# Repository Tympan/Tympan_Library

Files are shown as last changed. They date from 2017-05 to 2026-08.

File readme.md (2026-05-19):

Tympan Library
===========================



**Purpose**: This library allows you to program your own audio processing algorithms for the Tympan!  It owes a big debt to the [Teensy Audio Library](http://www.pjrc.com/teensy/td_libs_Audio.html) and all of its contributors.

**Note**: These instructions were based on the *Arduino IDE 1.8.15* and *Teensyduino 1.54*. If you have different versions of either of these or have downloaded different versions, the program may or may not function as expected. You may revert or upgrade to the stated versions or check for solutions on the [Tympan Forum](https://forum.tympan.org/).

Requirements
------------

**Hardware**: All versions of the Tympan are, at their heart, compatible with the Teensy brand of microcontrollers.  Hence, many of the instructions below relate to Teensy.  For reference, Tympan RevD is Teensy 3.6 whereas the Tympan RevE is Teensy 4.1.

**Arduino IDE (Windows/Linux)**:  To program the Tympan, you need to download and install the 1.8.x version of the [Arduino IDE](https://www.arduino.cc/en/Main/Software).  Scroll down and download the 1.8.x version, do not use the newer 2.x version nor the web-based editor. After installing the Arduino IDE, open the shortcut so that it fully initializes.  Then, you can close it down and move to the next step, which is...

**Teensyduino Add-On (Windows/Linux, MAIN branch)**:  After installing the Arduino IDE, you need to download and install the [Teensyduino Add-On](https://www.pjrc.com/teensy/td_download.html), which allows you to program Teensy devices (including Tympan) using the Arduino IDE. It'll ask you whether you want to install a bunch of libraries.  You can say "yes" to them all, or you can say "yes" to these few: Audio, Bounce2, FreqCount, FreqMeasure, i2c_t3, SerialFlash, Snooze, and SPIFlash.  

**Teensyduino (Mac, MAIN branch)**: Recent versions of OS X do not support the Teensyduino Add-On installer, so there is a full [Teensyduino IDE](https://www.pjrc.com/teensy/td_download.html) available from the Teensy project which just needs to be downloaded and extracted from its ZIP file.

Installing the Tympan Library
------------

**Know GitHub?**:  If you know GitHub, go ahead and fork this repo and clone it to your local computer.  I strongly recommend that you clone it directly to the place on your computer where the Arduino IDE looks for libraries.  On my computer, I put them here: `C:\Users\chipaudette\Documents\Arduino\libraries\Tympan_Library`

**Don't Know GitHub?**: If you don't know GitHub, no problem!  You can download this library as a ZIP file.  Go back to the root of the Tympan library ([here](https://github.com/Tympan/Tympan_Library)) and click on the green button that says "Clone or Download".  You can then select "Download Zip".  Once the download is complete, I'd unzip the files and put them where the Arduino IDE looks for libraries.  On my computer, I put them here: `C:\Users\chipaudette\Documents\Arduino\libraries\Tympan_Library`

Connect the Tympan Audio Board
------------------

Open or restart the Arduino IDE. Before you can compile programs, you will need to tell the Arduino IDE that you want to program for Teensy. Under the "Tools" menu, choose "Board" and then "Teensy 4.1" for Tympan RevE (choose "Teensy 3.6" for Tympan RevD).  Also, under the "Tools" menu, choose "USB Type" and select "Serial + MIDI + Audio". 

If you haven't already, plug in the Tympan Audio Board to your computer using the micro USB cable. You will see orange lights. Power the unit ON using the white switch on the side and you will see the blue blinking light which indicates power. If you already had the Tympan Audio Board plugged in, turn the power off and then on again to power cycle prior to proceeding. Make sure you see the message that the device drivers are being installed.

Once your Tympan is connected to the computer via the micro USB cable and powered on, you can select the device by choosing "Port" under the "Tools" menu and and select the one that is associated with the Teensy (on Windows, it'll say "Teensy" in its name).

Try Some Examples
-------------

In the Arduino IDE, under the "File" menu, select "Examples".  Then, scroll way to the bottom of the list.  You should see an entry that says "Tympan_Library".  Those are all the example files for trying out different audio algorithms or features of the system.  I recommend starting with the basic examples:

* **Audio Pass-Thru:**  You should start with this example.  No processing, just an audio pass-thru from input (microphone, pink socket) to output (headset or earbuds, black socket).  You should always start as simple as possible.  It doesn't get simpler than this.  Since it doesn't apply any gain, it'll be quiet.

Once the example has been selected, it needs to be compiled or uploaded. The Arduino IDE's compile button is the one with the Arrow facing to the right. Note: take headphones off your ears when uploading a new program or changing modes to avoid any sharp pops, clicks, or other unpleasant noises.

Once the basic audio pass-thru program works, you can try the next example:

* **Basic Gain:** As your second trial, you try this example, which adds gain to the audio.  The blue volume knob adjust the amount of gain.  Easy!  

While the Tympan is connected to your computer (via USB) and running the Basic Gain example, you can communicate with your Tympan to find out what it's doing.  Under the Arduino IDE's "Tools" menu, select "Port" and select the one that is associated with the Teensy (on Windows, it'll say "Teensy" in its name).  Once you've selected the Teensy's port, you can open the "Serial Monitor" from the "Tools" menu.  On the Tympan, you can turn its blue volume knob.  Looking at the Serial Monitor window, you can see that it reports the volume setting it's now using.  In the other example programs, the Serial Monitor is used extensively to monitor what the Tympan is doing.

Once this works, you can work your way down the examples list to see how they add complexity and capability.  Have fun!

Releasing Tympan_Library to Arduino Library Manager
-------------
The Arduino "Library Manager" is a handy way for some users to keep up-to-date with the Tympan_Library.  For those of us used to using Git/GitHub, be aware that users do not get the latest state of the repository.  Instead, the Arduino Library Manager will only people's libraries if we do a new "Release" here on GitHub.  For Arduino to accept the release, however, you must do the release correctly:

* Make your desired changes to the Tympan_Library:
  * Commit your software changes to the repo and push them up here to GitHub
* Arduino-Specific Changes:
  * In the file [library.properties](https://github.com/Tympan/Tympan_Library/releases/new), update the version number to whatever new version number you intend to use.  Commit the change and push the change up here to GitHub.  If you forget to do this, Arduino will ignore the release.
* Do the GitHub release in the usual way:
  * Go to [Draft a New Release](https://github.com/Tympan/Tympan_Library/releases/new)
  * Under "Choose a Tag", start typing a name that you want to use for this Release ("V3.0.6").  Be sure to also click "Create New Tag on Publish" to tag the repo at its current state, which is what the release will be built on.
  * Fill in field for "Release Name" and add some text describing what is in the release
  * Click the button "Generate Release Notes", which puts a listing of all the commits at the bottom of the release text
  * Click "Publish Release"

To check on the status of the Tympan_Library being accepted by the Arduino Library Manager, see the Arduino processing log here: https://downloads.arduino.cc/libraries/logs/github.com/Tympan/Tympan_Library/

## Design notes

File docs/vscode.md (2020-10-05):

# Using VSCode and Platform IO with your Tympan

In addition to using the Arduino/Teensyduino IDE for working your Tympan, it is possible to use VSCode and PlatformIO as a development environment. It does, however, require some customizations to your `platformio.ini` file that might not be immediately obvious. The process for configuring VSCode and Platform IO (after you have followed the main instructions in the readme) is roughly as follows:

1. If you do not already have it, [download VSCode](https://code.visualstudio.com/download)
2. Install the [PlatformIO IDE plugin in VSCode](https://marketplace.visualstudio.com/items?itemName=platformio.platformio-ide) (note: if you use Anaconda on a Mac, you will likely need to update or reinstall Anaconda)
3. Create a new project in the PlatformIO IDE (choose the `teensy36` board)
4. Add the following three libraries to the lib_deps option: `Tympan_Library`, `https://github.com/PaulStoffregen/Audio.git`, and `https://github.com/PaulStoffregen/SD.git` (note: these are the same libraries required by the Tympan Library itself)
5. Put the path to the `libraries` directory you located in the "Installing the Tympan Library" section of the [readme](../readme.md) in the `lib_extra_dirs` option
6. Make sure to follow the instructions that PlatformIO gives you to convert your `.ino` file into a `.cpp` file (basically renaming the file and adding some additional `#include` directives)
7. Connect your Tympan to your computer and turn it on
8. Click the "Run" (right-facing arrow) button in the status bar to run your sketch on the Tympan

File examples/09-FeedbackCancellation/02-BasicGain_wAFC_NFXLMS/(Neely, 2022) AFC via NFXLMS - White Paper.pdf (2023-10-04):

Adaptive Feedback Cancelation
Introduction
Figure 1 shows a framework for adaptive feedback cancellation (AFC). The desired input signal is x(n), the actual microphone is d(n), and the hearing-aid output is s(n). When there is feedback, the microphone signal d(n) contains the feedback signal y(n) in addition to the desired signal x(n). The feedback signal is generated by the hearing-aid output s(n) passing through a feedback path F(z). The goal of feedback cancellation is to obtain an estimate of the feedback signal, denoted as y+(n), and subtract it from the microphone signal d(n) (Kates, 2008). This is achieved by placing a finite impulse response filter W(z) in parallel with the hearing-aid processing G(z). W(z) served as an estimate of the feedback path F(z). Under adaptive feedback cancellation, the coefficients of filter W(z) are continuously updated with the goal of emulating the impulse response of the feedback path F(z). Under ideal conditions, the estimated feedback path W(z) matches the actual feedback path F(z). When this happens, the feedback-compensated signal matches the feedback signal, so that y+(n) = y(n), and e(n) = x(n), i.e., the input to hearing-aid processing will not contain any feedback. In practice, however, AFC is not perfect, and some mismatch remains between e(n) and x(n), resulting in audible distortions.

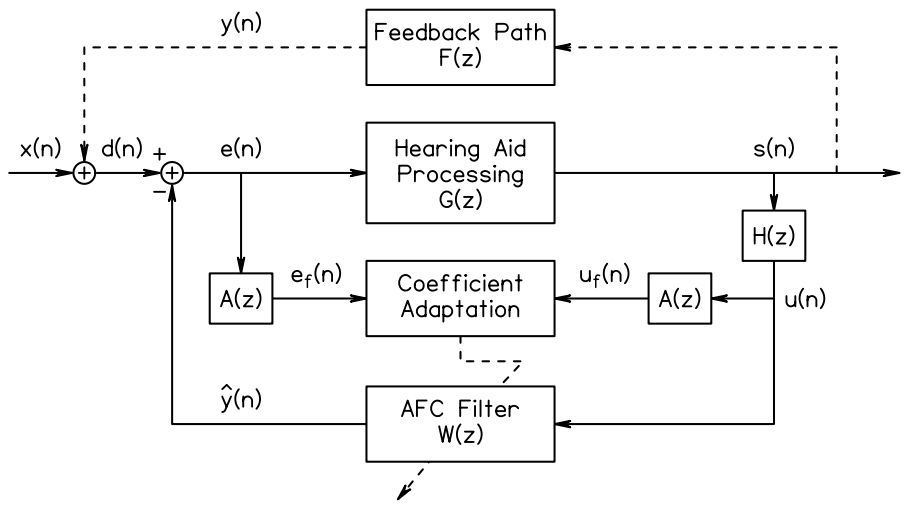
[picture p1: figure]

Fig. 1. Framework for adaptive feedback cancellation (Adapted from Lee et al. 2017). The actual and estimated feedback filters are F(z) and W(z), respectively. The whiten and band-limit filters are A(z) and H(z), respectively. The

The most common method for adaptive feedback cancellation is the least mean square (LMS) algorithm. Several LMS-based algorithms have been proposed, all of which include a step size parameter that controls how fast the AFC filter coefficients are updated. In the ordinary LMS algorithm, rapid fluctuations in the input signal can lead to instability. The normalized LMS (NLMS) algorithm mitigates some of the instability problems of the ordinary LMS algorithm by dividing the step size parameter by the signal power. For both NLMS and LMS coefficient adaptation method, the whiten and band-limit filters have unity gain, so A(z) = H(z) = 1. The normalized filtered-X LMS (NFXLMS) algorithms address some of the limitations of the NLMS method by (1) reducing non-feedback correlation and (2) concentrating adaptation on the frequency range where feedback is known to occur.

Normalized LMS
Normalized LMS (NLMS) is a variant of the LMS algorithm that improves stability by reducing sensitivity of coefficients to input signal level. The NLMS algorithm is based on cross-correlation between the output and input of the hearing-aid processing. The cross-product is weighted by a time-varying step size
w(n + 1) = w(n) + μ!(n)s(n)e(n).

The step is normalized by the signal power to improve convergence rate and stability
μ!(n) = "
℘(!)&' ,

where ℘(n) is a signal power estimate at time n and ε is a power-threshold parameter that prevents the denominator from becoming too small. In our implementation, the signal power is estimated by a first-order recursive equation
℘(n + 1) = ρ[s⁽(n) + e⁽(n)] + (1 − ρ)℘(n).

Note that the NLMS algorithm has three parameters: μ, ε, and ρ. Parameter values are optimized by minimizing the difference between the AFC filter W(z) and the feedback path F(z) in a simulated feedback configuration.
NFXLMS
When the NFXLMS algorithm is used to derive AFC coefficients the same calculations are performed as for NLMS except that u)(n) and e)(n) replace s(n) and e(n)

w(n + 1) = w(n) + μ!(n)u)(n)e)(n)

℘(n + 1) = ρ>u)

((n) + e)

((n)? + (1 − ρ)℘(n).

Additional filtering is required to obtain u)(n) and e)(n) from s(n) and e(n). Parameter values are optimized by minimizing the difference between the simulated feedback path F(z) and the product of W(z) and H(z). In practice, parameters are optimized by minimizing the mean-squared difference between the impulse responses f(n) and the convolution of w(n) and ℎ(n).

Whiten Filter
The whiten filter A(z) flattens the spectrum of the input signal x(n) to reduce correlation between the input signal and the hearing-aid output s(n). In our implementation, filter coefficients were derived from the long-term average speech spectrum (LTASS) described by Stelmachowicz (2000).
Figure 2 show the LTASS in the left panel and the inverted LTASS in the right panel (blue curve). The frequency responses of 5-tap and 9-tap linear-phase, FIR filters that approximate the inverse LTASS are superimposed (green and red curves). Each of these filters improve the AFC performance with relatively little increase in computational load.

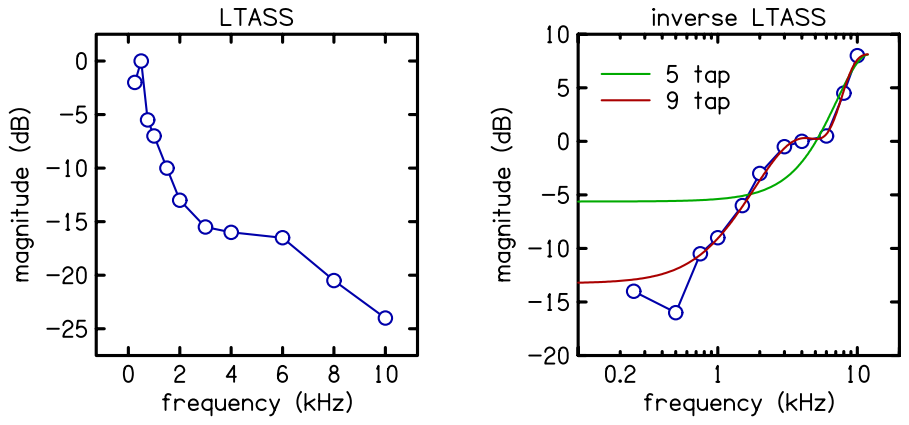
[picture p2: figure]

Fig. 2. Long-term average speech spectrum (LTASS) and its inverse. An inverse LTASS was constructed relative to the LTASS value at 4 kHz. The left panel superimposes 5-tap (green) and 9-tap (red) FIR approximations over the inverse LTASS (blue).
Band-limit filter
The motivation for the band-limit filter is to improve the efficiency of coefficient adaptation by focusing on the frequency range where feedback is known to occur. Our strategy is two-fold. First, we move some frequency dependence from W(z) to H(z). Second, we reduce the magnitude of H(z) at low frequencies where feedback is unlikely to occur.
The current implementation of the band-limit filter ℎ(n) has 36 taps and non-adaptive coefficients. The frequency response of the band-limit filter has a high-pass characteristic as shown by the green line in the right panel of Fig. 3. The effect of the band-limit filter on the AFC estimate of the feedback path is demonstrated in Fig 3 by observing that the estimated feedback (red) is closer to the actual feedback (black) in the right panel compared to the left panel.

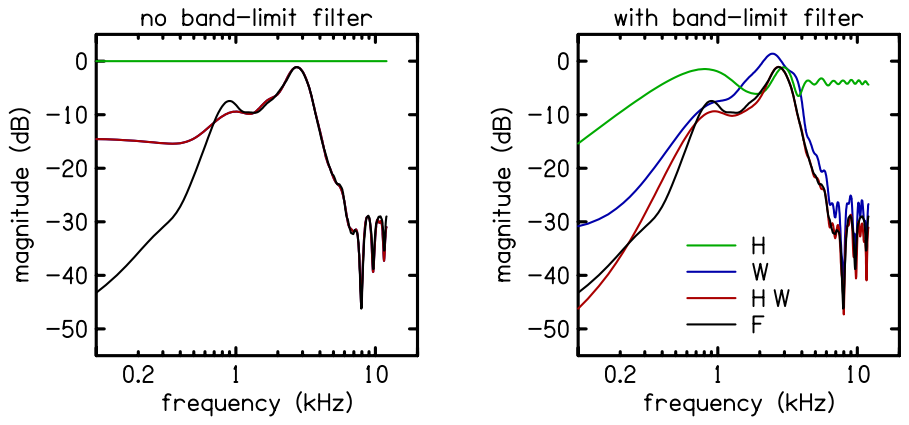
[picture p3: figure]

Fig. 3. Spectral magnitudes of the band-limit (H, green), AFC (W, blue), and feedback-path (F, black) filters. Also shown is combined response of the product of the band-limit and AFC filters (HW, red), which approximates the feedback-path filter. For the case without band-limiting (left panel), the band-limit filter has 0 dB gain at all frequencies. When band-limiting is applied (as described in the text), the combined response (red) better estimates the feedback-path (black) below 0.4 kHz and above 8 kHz.

Parameter Values
Optimization of parameter values was based comparison of the actual feedback path with the AFC estimate. An estimation error was defined as the mean-squared difference between the actual and estimated feedback-path impulse response. The estimation error was computed as a function of time for the “carrots” passage, which is 13 seconds long. Parameter values were selected (by a simplex search) to minimize the maximum error over the interval of time between 2 and 13 seconds. Figure 4 illustrates the parameter optimization procedure by comparing an example of actual and estimated feedback paths (left panel) and by showing an example of time course of the estimation error (right panel).

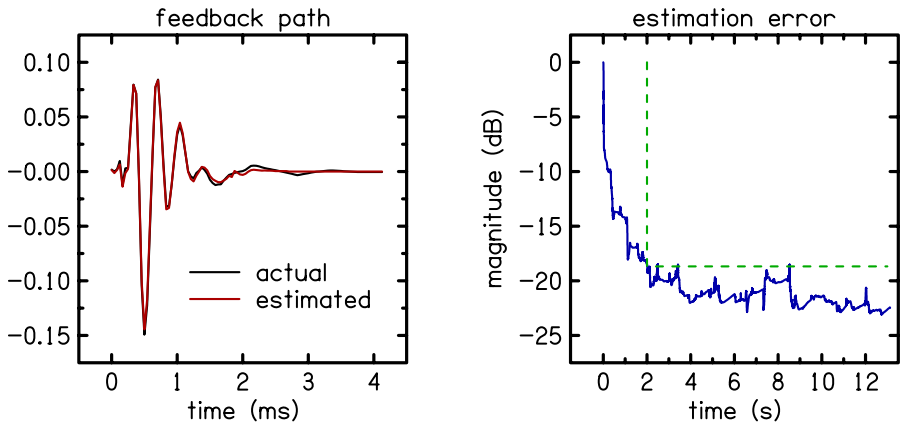
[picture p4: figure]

Fig. 4. Comparison of the actual (black) and estimated (red) feedback-path impulse responses (left panel) and the time course of the estimation error (right panel). The dashed (green) line (right panel) indicates the maximum-observed error over the interval of time between 2 and 13 seconds.
The four parameters optimized by this procedure appear in the equations used to calculate the AFC filter coefficients (μ, ε, ρ) and the band-limit filter coefficients (α). Filter lengths were also varied independently in a stepwise manner to further the estimation error. The following Table summarizes the results of parameter optimization.
AFC Filter | Whiten Filter | Band-limit Filter | ρ | ε | μ | Error (dB) | Comp time
42 | 0 | 0 | 0.000002 | 0.001395 | 0.000418 | -13.58 | 0.164
42 | 9 | 0 | 0.006840 | 0.001178 | 0.004693 | -15.27 | 0.165
42 | 9 | 20 | 0.007219 | 0.000919 | 0.004607 | -18.47 | 0.441

The first set of parameter values in the Table represent our NLMS algorithm which has no whiten or band-limit filters. The second set of parameters shows a reduction of 1.7 dB in the estimation error when a whiten filter is added to NLMS. The third set of parameters represents the addition of both whiten and band-limit filters, which represents our NFXLMS algorithm and shows a 5.2 dB reduction in estimation error relative to our NLMS algorithm. We hope to see a corresponding 5.2 dB improvement in added stable gain (ASG).

References
Kates, J. M. (2008). Digital hearing aids. Plural publishing, pp 175-220.
Lee, C. H., Kates, J. M., Rao, B. D., & Garudadri, H. (2017). “Speech quality and stable gain trade-offs in adaptive feedback cancellation for hearing aids,” J. Acoust. Soc. Am. 142, EL388-EL394.
Stelmachowicz, P. G. (2000). “How do we know we’ve got it right? Electroacoustic and audiometric measures,” in “A sound foundation through early amplification,” proceedings of an international conference, pp. 109-118.

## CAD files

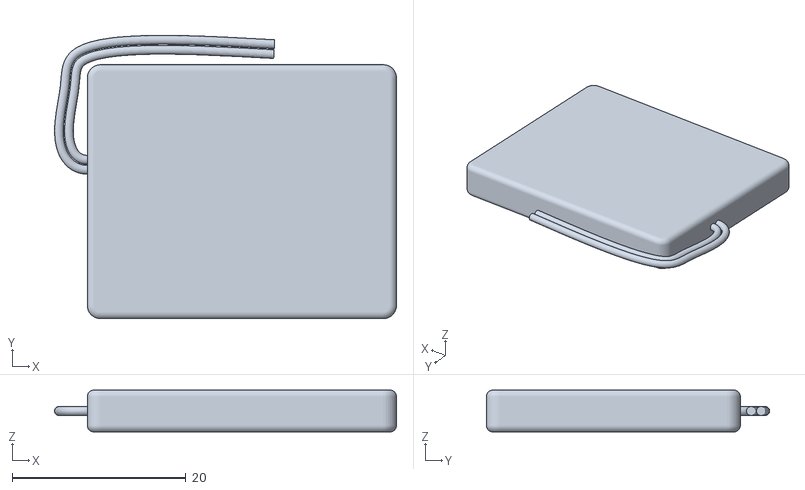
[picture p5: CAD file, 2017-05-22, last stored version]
hardware/Tympan_Enclosure/SolidModelOfPCB/Lion Ion Battery.stl
39.3 x 32.6 x 4.83

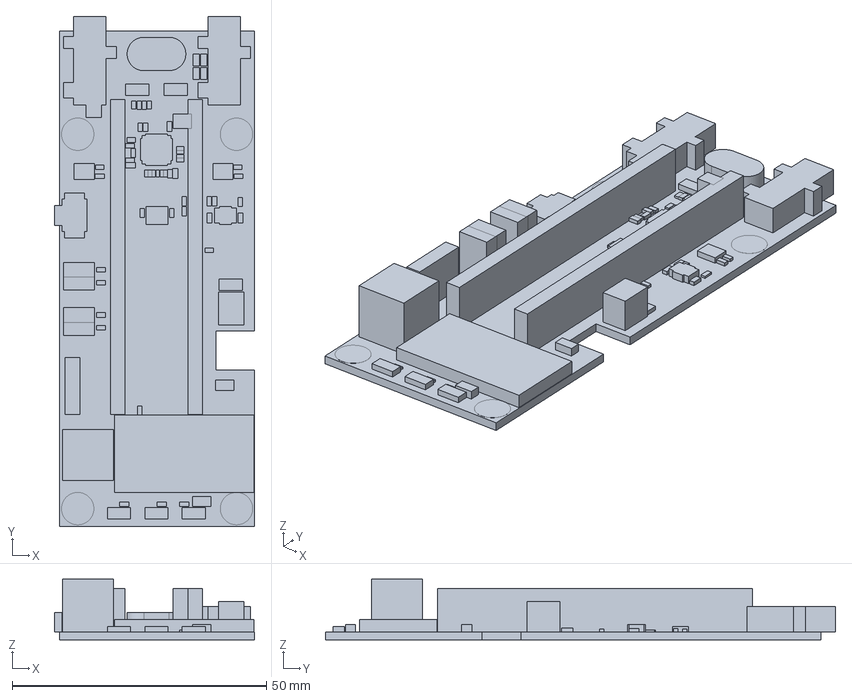
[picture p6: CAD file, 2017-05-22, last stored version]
hardware/Tympan_Enclosure/SolidModelOfPCB/7146-0012_PCB_Rev-A.STP
39.4 x 100.3 x 12.0 mm
BOARD_OUTLINE
COPAL_CL-SB-22A-1
RESC1609X50N x 4
SAMTEC_SSW-124-XX-X-S x 2
SAMTEC_SSW-104-XX-X-S
SAMTEC_SSW-101-XX-X-S
SLOT1000X500MECH
FUSC3216X78N
MTG_4 x 4
MICROCHIP_RN42
TP340X180N x 2
PH_B2B-PH-K-S
RESC0603X26N x 10
RESC100X50X40L25 x 2
RESC1005X40N x 8
SAMTEC_SSW-102-XX-X-S x 4
CAPC1005X55N x 13
LEDC3216X110N x 5
CAPC1005X70N x 5
CAPC1005X65N x 8
BOURNS_3386F-KNOB
CUI_SJ-3523-SMT
CUI_SJ-3524-SMT
SOT23-5P95_270X145L35X35
SOT95P280X145-5N
KNOWLES_SPH1642HT5H-1 x 2
QFN40P500X500X80-41N

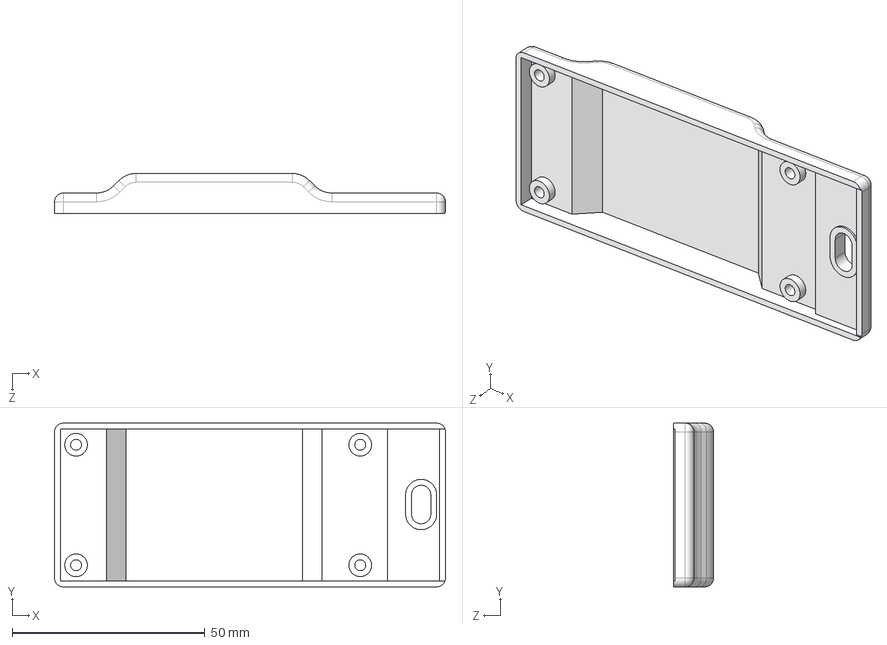
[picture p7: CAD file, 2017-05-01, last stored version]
hardware/Tympan_Enclosure/STEP/10000167 rev3.step
101.3 x 42.4 x 10.4 mm

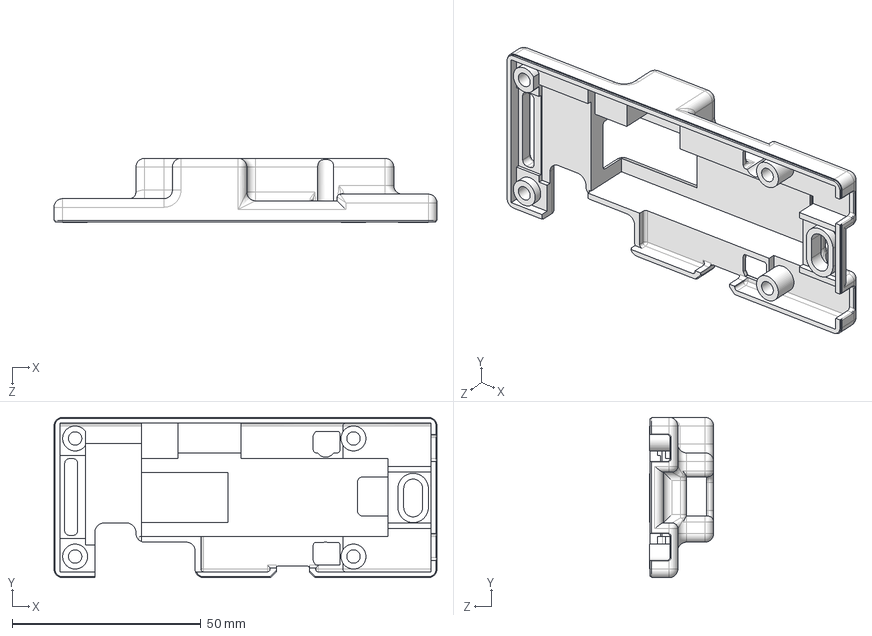
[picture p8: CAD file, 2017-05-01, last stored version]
hardware/Tympan_Enclosure/STEP/10000200_r2.step
101.3 x 42.4 x 17.0 mm

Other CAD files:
hardware/Tympan_Enclosure/SolidModelOfPCB/Lithium Ion Battery.step
hardware/Tympan_Enclosure/STL/10000167 rev3.stl
hardware/Tympan_Enclosure/STL/10000200_r2.stl

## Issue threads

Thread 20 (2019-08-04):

Tympan/Tympan_Library #20: failed build with 05-FullSystems/* example sketches, one error and others too large

shapr, 2019-08-04:
I'm using Ubuntu 19.04 with Arduino 1.8.9 and Teensyduino 1.46
and the very latest git clone of Tympan_Library

I've failed to compile all of the 05-FullSystems/*

* WDRC_8BandFreqWarpFIR:45: error: 'audioTestMeasurement' was not declared in this scope AudioControlTestAmpSweep_F32    ampSweepTester(audio_settings,audioTestGenerator,audioTestMeasurement);
* File "WDRC_8BandIIR_wBT.ino.hex". 74520 bytes, 116% used
* File "WDRC_8BandIIR_wBT_wAFC.ino.hex". 89688 bytes, 139% used
* File "WDRC_8BandFIR_wBT.ino.hex". 85568 bytes, 133% used
* File "WDRC_8BandFIR.ino.hex". 85056 bytes, 132% used
* File "WDRC_3BandIIR_wBT_wAFC.ino.hex". 88672 bytes, 137% used

I haven't dug into the actual compile error, but the others all claim they resulting sketch is too large to fit onto the chip.
Perhaps this is something to do with the Teensyduino 1.46 update?

chipaudette, 2019-08-05:
I'm sorry for the basic question back to you...but In the Arduino software, under the "Tools" menu, did you change your "Board" to "Teensy 3.6"?  

Chip

chipaudette, 2019-08-05:
Also, I fixed the error with the WDRC_8BandFreqWarpFIR as of commit f9d82558f8304a24e2d246bbf261f2f0a3855493

Good find!

As for the memory issue, please see my comment above.  If you're not set for Teensy 3.6, it is very easy to see how it thinks you won't have enough memory.

Chip

shapr, 2019-08-06:
I fired up the Arduino IDE and checked my settings (I'm using WDRC_8BandIIR_wBT since I believe that's the default firmware).
I do have the "Teensy 3.6" board selected (basic questions are fine, I make mistakes all the time!)
In the process, I discovered the Arduino menu has "Tools" -> "Optimize" and the "faster" option was selected. Once I selected "smallest", the Teensyduino loader stops complaining.

Should the code fit on the board with the "faster" option selected? 
I also tried "fast" and "fastest" but once the hex file reaches the teensyduino loader I get "too large".

chipaudette, 2019-08-08:
I finally found someone here who uses Ubuntu.  We're going to try to recreate your problem...

jdw-creare, 2019-08-08:
@shapr , I was able to reproduce your issue.  I've reported it to the Teensy maintainers here: https://github.com/PaulStoffregen/Arduino-1.8.9-Teensyduino/issues/3

closed 2019-09-28 by wheresaddie

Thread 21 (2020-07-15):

Tympan/Tympan_Library #21: External Delay

finnwoodman, 2020-07-15:
Hej Tympan Crew, 
I just stumbled across your incredible audio board. It looks like the perfect alternative for what I am doing with the teensy audio board right now. I was wondering whether Tympan has the capabilities to use something to Teensy Audio's AudioEffectDelayExternal. This allows creating longer lasting delays by using additional memory – either placed on the pcb directly or by incorporating a custom memory board. 
Best regards, Max

biomurph, 2020-07-15:
@finnwoodman @chipaudette 
So glad you found us!
I'm pinging Chip, who will be able to help answer.
Tympan works with the teensy audio library, and we have an SD card slot on board, if that is fast enough for your needs. If SD is too slow, we have breakout pins for the SPI bus, so you can lash up a flash memory chip or other.

What is your project and speed/memory needs?

finnwoodman, 2020-07-15:
Thank you for your fast reply. I guess SD card will be to slow as I am processing live sound. So, what I want to create is a 2sec echo loop of a microphone input. The overall goal is creating a kind of simple loop machine.

I managed to create such a "Machine" using the teensy audio board and external ram. Nevertheless I am facing a lot of noise. Tympan looks promising regarding noise and co...

biomurph, 2020-07-15:
Great video!
And great machine.

Adafruit has a couple flash breakouts. Here's one
https://www.adafruit.com/product/1895
It's I2C, and we've broken out the I2C on the Tympan. Note the lower left corner of the Tympan D [schematic](https://github.com/Tympan/Tympan_Rev_D_Hardware/blob/master/TympanRevDschem.pdf) which corresponds to the pinout looking down on the Tympan board. There are lots of development modules that use SPI as well if you really need speed.

I've had parts on my bench for a while to build an effects pedal with a Tympan D. Sparkfun has a nice [kit](https://www.sparkfun.com/products/13124) and I plan to use a flash memory chip in it. Just need the time to work out the power supply...

chipaudette, 2020-09-09:
@finnwoodman, currently the hardware has no place to add external memory.  So, you have the same memory as a Teensy 3.6.

If you need additional RAM, you'll need a product like the blackaddr Teensy Guitar Audio Shield: http://blackaddr.com/products/.  It has options that you can include when you place your order to add a 4Mbit or 8Mbit memory IC.

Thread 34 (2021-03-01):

Tympan/Tympan_Library #34: USB audio not supported

hriday91, 2021-03-01:
Currently USB audio in/out is not supported by tympan. Any idea on when will it be supported?

chipaudette, 2021-03-01:
Hi!  

USB audio could be supported as long as you always use a 44kHz sample rate with 128 points per audio block.  Its this inflexibility in the underlying Teensy USB audio system that is the problem.

Would 44 kHz / 128 points meet your needs?

Chip

chipaudette, 2021-06-10:
I would like to wrap the Teensy's USB audio class in a Tympan "_F32" wrapper.  I did this before, but it would cause compiler warnings if you didn't set your Arduino IDEA to have the "USB Type" include audio.  Since most people didn't use the USB audio, this was an annoying warning, so I pulled the _F32 wrapped USB audio class out of the Tympan Library

I think that there is a way for our code to listen compiler flags to avoid these warning messages so that we know if USB Audio has been set in the Arduino IDE.  If I can find out how to do that, we can put the _F32 USB audio class back in our library.

It's on the To-do list, for sure.

nithinr07, 2021-06-21:
Hi,

I am trying to add an AudioOutputUSB block to the single-channel WDRC code. However, this code can't really run well on the Rev D with the 44.1kHz and 128 block size setting, so I was wondering if there is any way to send the audio through USB at lower sampling rates.

Thanks!

chipaudette, 2021-06-21:
The USB audio functionality is the exactly the same code as the Teensy Audio Library USB audio code.  That code is limited to 44.1kHz and 128-sampke block size.  Sorry.

Does the FreqDomainDemo example that I linked above work ok?  Is your problem occur only when you use the USB audio with the WDRC?

nithinr07, 2021-06-21:
Yes, as long as the sampling rate is 44.1KHz and the audio block size is 128, it works, but unfortunately, the 8 band WDRC code can't support this on the Rev D I believe.

chipaudette, 2021-06-21:
You are correct.  the 8-band WDRC consumes too much CPU to be performed at 44 kHz.  If you want the USB audio, you will have to use fewer bands.

There is a group in Montreal that is looking to dig deep into the Teensy Tympan USB Audio code (and, therefore, the Tympan USB Audio code) to make it more flexible so that it can support different sample rates.  If they do it, I believe they are planning on doing it in July - September.

nithinr07, 2021-06-21:
Also, just to point out, I noticed that there were distinct "clicks" in the USB output when the sampling rate was 44100 Hz. However, this problem was solved when I changed the sampling rate to 44117 Hz.

chipaudette, 2021-06-21:
Yes, the requirement for 44117 is part of the limitations (and odd behaviors) that come with the Teensy audio library.  

Sorry.

nithinr07, 2021-06-28:
Hello again!

So, I managed to make the Tympan run at 24,000 Hz / 128 sample block size by tweaking the Teensy library (the USB descriptors), but I wasn't able to lower the block size. I noticed that the WDRC code performs best at lower block sizes, so I was wondering if you could provide me with any leads regarding this. 

Nithin

chipaudette, 2021-06-28:
Wow!  Congratulations on gettng the lower sample rate to work over USB!  Very impressive!

As for shorter block sizes, the WDRC is actually more computationally efficient (ie, less CPU consumed) for the larger block sizes like 128.  What works better is that the latency (the delay) of the audio passing through the system is reduced if the block size is made smaller.  

Do you care about latency?

  * If you do NOT care, than your 128-point block size should be great!
  * If you do care, then you should look into changing the Teensy header file [AudioStream.h](https://github.com/PaulStoffregen/cores/blob/adca415331771bbf1560d7a008ccb150b0ec603a/teensy3/AudioStream.h).  Change AUDIO_BLOCK_SIZE from 128 to something smaller (and change the Tympan code to match) and it might work for you.

Let me know how it goes!

Chip

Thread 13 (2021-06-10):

### ISSUE TITLE
No delay needed after Wire.write().

### ISSUE THREAD

**Issue by Koepel** [Tympan/Tympan_Library#13]
In the file "Tympan_Library/src/control_tlv320aic3206.cpp", there is sometimes a delay() after a Wire.write(). I think that delay() can be removed.

It is similar to this:
```
int i = 3;
delay(10);  // wait until i becomes 3
int j = 5;
delay(10);  // wait until j becomes 5
```

In the Arduino Wire library and in most Arduino Wire compatible libraries, a buffer is used. The Wire.beginTransmission() resets the buffer, the Wire.write() fills the buffer and the Wire.endTransmission() does the complete I2C transaction with START, I2C address, write data from the buffer and STOP.

I took a quick glance at the TLV320AIC3206 datasheet, but I can't read that a delay would be needed somewhere.

**Comment by chipaudette** [comment]
Over the last several years, I think that we have now pulled out most of the delay() calls.  There are a few delay() calls left in there, but they are mostly after register settings that change how the hardware functions, so they are there to let the hardware settle.

I think that this is complete.

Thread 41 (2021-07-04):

Tympan/Tympan_Library #41: Wrong register values for Mic Bias

eyuan-creare, 2021-07-04:
Value for 1.7V mic bias is not offset to the correct bits

Here is the register for Mic Bias (AIC3206), showing bias voltage as bits D5-D4. For example, to set Mic Bias to 1.7V, we need `TYMPAN_MIC_BIAS_POWER_ON   |  0b0001 0000`

[image]

- However in [Tympan Library](https://github.com/Tympan/Tympan_Library/blob/c44b8c3d6fce48084498e54583e6e4b5d78af186/src/control_aic3206.cpp#L162) the values are not shifted to the correct bits, either in the #define or the wrapper function 
```
#define TYMPAN_MIC_BIAS_REG 0x0133 // page 1 reg 51
#define TYMPAN_MIC_BIAS_POWER_ON  0x40
#define TYMPAN_MIC_BIAS_POWER_OFF 0x00
#define TYMPAN_MIC_BIAS_OUTPUT_VOLTAGE_1_25     0x00
#define TYMPAN_MIC_BIAS_OUTPUT_VOLTAGE_1_7      0x01
#define TYMPAN_MIC_BIAS_OUTPUT_VOLTAGE_2_5      0x10
#define TYMPAN_MIC_BIAS_OUTPUT_VOLTAGE_VSUPPLY  0x11
```

- Here is the [setMicBias](https://github.com/Tympan/Tympan_Library/blob/c44b8c3d6fce48084498e54583e6e4b5d78af186/src/control_aic3206.cpp#L287) function.  When 1.7V is selected this results in a value of `0b0100 0001` instead of 0b0101 0000
` aic_writeAddress(TYMPAN_MIC_BIAS_REG, TYMPAN_MIC_BIAS_POWER_ON | TYMPAN_MIC_BIAS_OUTPUT_VOLTAGE_1_7); // power up mic bias
`
So I believe the way it is now, if you select 1.25V that's fine.  But if you select 1.7, 2.5V, or the power supply, then you actually get 1.7V, with bit-0 set (which is reserved) 

@chipaudette perhaps you can double-check this, then I will branch off to make these corrections.  Does this mesh with the behavior you've seen?

eyuan-creare, 2021-07-04:
I don't think it is worth changing for the AIC3212, but I would typically use enums [here](https://github.com/Tympan/Tympan_Library/blob/c44b8c3d6fce48084498e54583e6e4b5d78af186/src/control_aic3206.h#L32).  This allows coders to quickly look up the enum from the function's input argument, and ensures that only the correct range of values are used.  With #defines, it is difficult to search for which define to use, unless you go off an example.
```
//names to use with setMicBias() to set the amount of bias voltage to use
#define TYMPAN_MIC_BIAS_OFF             0
#define TYMPAN_MIC_BIAS_1_25            1
#define TYMPAN_MIC_BIAS_1_7             2
#define TYMPAN_MIC_BIAS_2_5             3
#define TYMPAN_MIC_BIAS_VSUPPLY         4
#define TYMPAN_DEFAULT_MIC_BIAS TYMPAN_MIC_BIAS_2_5
```

to 

```
typedef enum {
    off, 
    Mic_Bias_1_25V, 
    Mic_Bias_1_70V,
   ...
} Mic_Bias_Values_t;
```

then in the function...

```
bool AudioControlAIC3212::setMicBias(Mic_Bias_Values_t biasSetting) {
  switch (biasSetting){
        case Mic_Bias_1_25V:
           aic_writeAddress(TYMPAN_MIC_BIAS_REG, TYMPAN_MIC_BIAS_POWER_ON | TYMPAN_MIC_BIAS_OUTPUT_VOLTAGE_1_25); // power up mic bias
          break;
    }
}
```
<br><br><br>
To take it a step further, I would encode the register value for mic bias voltage like this:
```
typedef enum {
    uint8_t Mic_Bias_1_25V = 0x00, 
    uint8_t Mic_Bias_1_70V = (0x01<<4) ,
    ...
} Mic_Bias_Voltage_t;
```

then in the function:
```
bool AudioControlAIC3212::setMicBias(Mic_Bias_Voltage_t biasSetting) {
    uint8_t regValue = 0;

    // Read in what's there to preserve the other bits 
   regValue  =  aic_ReadAddress(TYMPAN_MIC_BIAS_REG);

   // Mask out the desired bits to change
   regValue &= (~MIC_BIAS_VOLTAGE_BIT_MASK); 
  
    // Write the new register value
    aic_writeAddress(TYMPAN_MIC_BIAS_REG, regValue | biasSetting);
}
```
I think this is much cleaner.

eyuan-creare, 2021-07-04:
In regards to the AIC3212, it uses different mic bias voltage.  Is that an issue with any of our mics?

[image]

chipaudette, 2021-07-04:
We've only ever used the full bias voltage (2.2v?), so these other voltage values have never ended up being an issue.  It's good to get them correct, but it's not yet been revealed as a problem die to always using the full voltage.  

I agree that an enum send better.  Someone else did the initial code where #define was used instead of enum.  Enum seems better.

Chip

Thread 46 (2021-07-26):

Tympan/Tympan_Library #46: BluetoothAudio_PassThru - Cannot Connect RevE

hgeithner-creare, 2021-07-26:
The Tympan RevE does not show up as an audio device on the phone (Android/iOS) when the BluetoothAudio_PassThru sketch is loaded on the Tympan.

Testing instructions:

- Open your phone's Bluetooth control panel and connect to the Tympan manually
- Open any audio-related app on your phone (or a browser and then to YouTube)
- Play something with audio
- Plug headphones in the Tympan and you should hear your phone's audio through the Tympan
- The volume buttons on your Phone should affect the phone's audio coming out of the Tympan

At the same time, you should be able to tap on the case of the Tympan and hear the Tympan's own microphones mixed with the BT audio.

chipaudette, 2021-07-26:
With the v5 firmware for the BC127, I got bluetooth audio to work simply by invoking the sparkfun library, which is discussed in their helpful tutorial here:

https://learn.sparkfun.com/tutorials/understanding-the-bc127-bluetooth-module/all#usage-examples

It says that they used the Advanced Audio Distribution Profile (A2DP) and Audio/Visual Remote Control Profile (AVRCP) profiles to do the remote audio connection.  It's likely that only A2DP is needed to make the audio flow if one is always driving the play/stop/volume from the phone itself (rather than having the Tympan itself command "play" or "stop" of the audio, which is done via AVRCP).

In the v7 firmware, maybe some other protocol is better, but I'd start by looking at how to enable A2DP.

chipaudette, 2021-07-26:
Melody (ie, BC127 Firmware) V7 Documentation for A2DP:
 
[image]

chipaudette, 2021-07-26:
It looks like that "SET PROFILES=0 0 1 0 1 0 0 0 0 0 0 0" is the key line that we need to convey during initialization of the BC127.  What does each zero or one correspond to?  According to the table below, it permits one A2DP sink connection and one AVRCP connection.

[image]

chipaudette, 2021-07-26:
Based on the table above, it looks like "A2DP sink" should already be enabled (has a "2").  Why doesn't it?

chipaudette, 2021-07-26:
Apparently A2DP is an BT Classic feature whereas we have been (recently) only focusing on BLE.  We enable BLE connections by commanding "ADVERTISING ON" but this does nothing to enable the classic BT connections.  Therefore, we must also enable the BT classic modes to be connectable and discoverable via the command:

`BT_STATE ON ON

This is necessary for the V7 firmware.  I'm not sure about the V5 firmware.

hgeithner-creare, 2021-07-26:
I'm not sure that it would be necessary for the V5 firmware because I was able to connect the RevD.

chipaudette, 2021-07-26:
Ray already included a command for "discoverable()" in the BC127 library.  This command only works for V5.  I extended it for V7.  I also altered the BLE class to initialize the module to make it discoverable (BT classic) by default upon startup (and anytime, actually). 

Changes are on feature_BTaudio branch.

This enables a simultaneous BT audio and BLE connection.  The problem is that it still won't receive audio (on my BC127 HD running V7.3HD).  Whenever I start to stream audio to it, the module appears to reset.  :(

chipaudette, 2021-07-26:
It appears that the unit defaults to allow for the GPIO pins to control the system operation, such as when sinking audio.  Since I am not consciously controlling the BC127 pins, maybe it is getting confusing commands?  Let's try disabling the GPIO control via (v7 firmware):

`SET GPIO_CONFIG=OFF 0`

Then write then reset.

Now, the BC127 seems to lock up instead of just resetting.  I have to cycle the power to get the BC127 to respond again.

chipaudette, 2021-07-26:
When you set GPIO_CONFIG to "off", it doesn't disable GPIO control, it merely alters it...one pin is still an input:

[image]

chipaudette, 2021-07-26:
On RevE, PIO 4 is not connected to anything...meaning it is floating...meaning it is high impedance...meaning the BC127 should be fine with driving it as an output.

PIO 0 and PIO 5 are connected to pins on the Teensy.  When I manually configure them so that the Teensy treats PIO 0 as an input (ie, makes it high impedance) and treats PIO 5 as an output set low (ie, forces it to exit data mode), the system no longer freezes when I start streaming audio.   Instead, it merely returns to the same behavior as before...it fails to stream (ie, no audio comes out the headphone jack) and it stops my phone music app after ~3 seconds.

Still in search of a solution...

chipaudette, 2021-07-26:
I'm stumped.  Here's my test method:

I'm using the example sketc below, based on BC127Terminal, but with added '\r' -> '\n' reformatting to allow use of the Arduino Serial Monitor:

```
/*
*	BC127Terminal
*
*	Created: Ira Ray Jenkins, Creare, December 2020
*	Purpose: Demonstrates a serial terminal with the BC127 module.
*
*/

#include <Arduino.h>

usb_serial_class *USB_Serial;
HardwareSerial *BT_Serial;

void echoIncomingUSBSerial(void)
{
    while (USB_Serial->available())
    {
        BT_Serial->write(USB_Serial->read());
    }
}

void echoIncomingBTSerial(void)
{
  char c;
    while (BT_Serial->available())
    {
      c = BT_Serial->read();
      if (c == '\r') c = '\n'; //replace carriage return with newline to make pretty in Arduino Serial Monitor
      USB_Serial->write(c);
    }
}

void setup()
{
    //  myTympan.beginBothSerial();
    Serial.begin(9600);
    Serial1.begin(9600);
    USB_Serial = &Serial;
    BT_Serial = &Serial1;

    Serial.println("Setting GPIO pins that are connected to BC127 assuming SET GPIO_CONTROL=OFF 0");
    pinMode(2,INPUT);  digitalWrite(2, LOW); //RevE PIO5
    pinMode(5,OUTPUT);//RevE PIO0

    Serial.println("Type commands to send to the BC127.  Be sure to use carriage return, not newline...");
}

void loop()
{
    echoIncomingUSBSerial();
    echoIncomingBTSerial();
}
```
Test Steps with RevE (with V7.3HD firmware):

0) The first time you do this, have your phone "forget" your Tympan BT unit
1) Compile and upload the sketch.
2) Open the Serial Monitor
3) Type Status.  Do you see `STATE CONNECTED[0] CONNECTABLE[ON] DISCOVERABLE[ON] BLE[IDLE]`.  If not:
    * type: SET BT_STATE_CONFIG=1 1
    * optionally, type: SET GPIO_CONFIG=OFF 0
    * type: WRITE
    * Type: RESET
4) Pair your phone and Tympan (the first time)
5) In your phone's BT control panel, connect to the Tympan
6) In the serial monitor, you should have seen stuff happen.  Type STATUS to see the connections
7) Open a music player app on your phone and stream music

Assuming that it fails for you, like it did for me...It should run for a ~3 seconds before the app switches to pause.  In the serial monitor, you should see the startup text, like:

```
Sierra Wireless Copyright 2018
Melody Audio V7.3 HD
Build: 1544717993
Ready
CHARGER_DISABLED
```

Bummer.

ijenkins-creare, 2021-08-04:
@hgeithner-creare , Haley, could you create a new sketch from Chip's example above. Compile for the RevE:v7. Once running, bring up the serial monitor, change the newline to carriage return (the dropdown menu left of "Clear output"). All of the following commands are entered via the serial monitor input line.

Enter "STATUS". You should see something like: 
```
STATE CONNECTED[0] CONNECTABLE[OFF] DISCOVERABLE[OFF] BLE[IDLE]
```

If not, what do you see? Try a "RESTORE" command.

Next, toggle BLE mode on with the command "ADVERTISING ON". Should see "OK". Check that the "STATUS" changed.

At this point, you should be able to connect to the Tympan from a phone/tablet via BLE. Assuming that connection is fine, you should see something like:
```
OPEN_OK 14 BLE 63F5A35DDBB5
```
Next, you can enter the command "BT_STATE ON ON", and again check your phone/tablet for bluetooth connections. You should see the same device name, but with *maybe* a different icon? Try to connect to it. Hopefully it spits out something like:
```
OPEN_OK 23 HFP 90B1445F6B2C
ROLE_OK 90B1445F6B2C M
OPEN_OK 20 A2DP 90B1445F6B2C
ROLE_OK 90B1445F6B2C M
A2DP_STREAM_START 20
OPEN_OK 21 AVRCP 90B1445F6B2C
ABS_VOL 21 77
A2DP_STREAM_SUSPEND 20
AVRCP_PAUSE 21
A2DP_STREAM_START 20
AVRCP_PLAY 21
```
Play some music or video files. You won't be able to hear audio, but you should see in the serial monitor that "something" happens. Let it play for a minute, making sure the phone doesn't pause the video/audio and the serial monitor doesn't "stall". You can periodically type "STAUS" just to make sure it's still alive, if you like.

Thanks!

hgeithner-creare, 2021-08-05:
@ijenkins-creare I load the example sketch and the STATUS looks good:

```
08:49:19.989 -> Setting GPIO pins that are connected to BC127 assuming SET GPIO_CONTROL=OFF 0
08:49:19.989 -> Type commands to send to the BC127.  Be sure to use carriage return, not newline...
08:49:19.989 -> STATE CONNECTED[0] CONNECTABLE[OFF] DISCOVERABLE[OFF] BLE[IDLE]
08:49:20.082 -> OK
```
BLE ADVERTISING successful: 

```
08:49:40.582 -> OK
08:49:54.607 -> STATE CONNECTED[0] CONNECTABLE[OFF] DISCOVERABLE[OFF] BLE[ADVERTISING]
```

When I pair the device:

```
08:50:51.202 -> OPEN_OK 14 BLE 5A2AF556C6FE
08:50:51.342 -> PAIR_PENDING
08:50:56.606 -> PAIR_OK D4E6B726F4F8
08:50:56.653 -> BLE_PAIR_OK 5A2AF556C6FE D4E6B726F4F8
```

When I typed "BT_STATE ON ON" I only got "OK" as the return message. I asked for "STATUS" again:

```
08:56:10.854 -> STATE CONNECTED[0] CONNECTABLE[ON] DISCOVERABLE[ON] BLE[CONNECTED]
08:56:10.948 -> LINK 14 CONNECTED BLE 5A2AF556C6FE 23
08:56:10.995 -> OK
```

The device shows up twice in the Bluetooth settings. The icons are different:

[image]

I couldn't get the Tympan to connect - only pair (there is a difference right?) I never heard audio streaming or saw anything in the serial monitor.

chipaudette, 2021-08-22:
We think that this is taken care of by Merge #52 .

closed 2021-08-22 by chipaudette

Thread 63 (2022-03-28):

Tympan/Tympan_Library #63: Audio noise reduction not working

michaelliesenberg, 2022-03-28:
Hi,

i am trying to use the tympan library for my custom board. I use the TLV32ßADC6140 and everything is working fine.

I have a stereo input at 192kHz and i do an average down to 48kHz and after that i am trying to do a noice reduction but the audio output is zero.
If i uncomment "#define FFT_Noise_Subtraction", everything is working fine, but using the noise subtraction algorithmus i dont see any audio signal output.  

Here is my code:

````
#include <Arduino.h>
#include "Filter_FFT.h"
#include <stdio.h>
#include <Tympan_Library.h>
#include "AudioEffectNoiseReduction_FD_F32.h"

#define FFT_Noise_Subtraction //If i turn this off everything is working fine
#define fiter_low_high_befor_FFT
#define fiter_low_high
#define AVG
#define PHASE_GAIN_CORRECTION

elapsedMicros sincePrint;
int helptime=0;

//set the sample rate and block size
const float sample_rate_Hz = 48000.f;   //24000 or 44117 (or other frequencies in the table in AudioOutputI2S_F32)
const int audio_block_samples = 128;       //for freq domain processing choose a power of 2 (16, 32, 64, 128) but no higher than 128
const int FFT_overlap_factor = 1;         //2 is 50% overlap, 4 is 75% overlap

AudioSettings_F32 audio_settings(sample_rate_Hz, audio_block_samples);
AudioEffectNoiseReduction_FD_F32    noiseReduction_right(audio_settings);
AudioEffectNoiseReduction_FD_F32    noiseReduction_left(audio_settings);

FFT_Overlapped_F32 myFFT_Right;
FFT_Overlapped_F32 myFFT_Left;
IFFT_Overlapped_F32 myIFFT_Right;
IFFT_Overlapped_F32 myIFFT_Left;
audio_block_f32_t *myBlock_Right;
audio_block_f32_t *myBlock_Left;

audio_block_f32_t* allocate_f32_memory_help(const int num) {
  static bool firstTime=true;
  static audio_block_f32_t *data_f32;
  if (firstTime == true) {
    firstTime = false;
    data_f32 = new audio_block_f32_t[num];
  }
  return data_f32;
}

Filter_FFT::Filter_FFT(int samplerate , int oversample, DATASTRUCT &datastruct): AudioStream(2,inputQueueArray)
{
  myData = &datastruct;
  
  dataReady=false;
  count=0;
  countAVG=0;
  SAMPLE_RATE=samplerate;
  oversampling = oversample/samplerate;
  STATE = average;

  left=NULL;
  right=NULL;

 
  int freq_hp = 100;//70 100
  int freq_tp = 2000;

  lowpass_average = new Dsp::FilterDesign<Dsp::Butterworth::Design::LowPass <order_lp>, 2, Dsp::DirectFormII> ;
[... 236 lines cut ...]
  
  params[0] = SAMPLE_RATE; // sample rateoutput
  params[1] = order_hp; // order
  params[2] = value;//25 // cutoff frequency
  highpass_second->setParams (params);  
}

void Filter_FFT::IQ_phase_correction (float32_t *I_buffer, float32_t *Q_buffer, float32_t factor, uint32_t blocksize)
{
  float32_t temp_buffer[blocksize];
  if (factor < 0.0)
  { // mix a bit of I into Q
    arm_scale_f32 (I_buffer, factor, temp_buffer, blocksize);
    arm_add_f32 (Q_buffer, temp_buffer, Q_buffer, blocksize);
  }
  else
  { // // mix a bit of Q into I
    arm_scale_f32 (Q_buffer, factor, temp_buffer, blocksize);
    arm_add_f32 (I_buffer, temp_buffer, I_buffer, blocksize);
  }
} // end IQ_phase_correction

````

Any idea?

chipaudette, 2022-03-28:
Hi,

You have a lot happening in your code, so it's hard to know what is going wrong.  Here are some thoughts:

* You have the line `const int FFT_overlap_factor = 1;`.  Presumably, you are setting this to 1 because you want no overlap of your FFTs.  I have never done this.  I have only used 2 or 4.  If you switch to 2, does it work?

* In your constuctor, you have the line `AudioMemory_F32(30, audio_settings);`.  This should not go here.  It should be called only once and it should be placed in your programs overall "setup()" function.  (Also, given how many operations you are doing in the frequency domain, you might want to increase this value to 60, instead of 30.  This  is just a guess.)

* I see that you use `complex_2N_buffer[0]` and `complex_2N_buffer[1]`.  I see where you allocate the memory for these two arrays via the `new` command, which is great.  But, where is `complex_2N_buffer` created?  Where is a line line `float* complex_2N_buffer[2];`?

* In your `update()` method, I see that you receive the `left` and `right` data blocks but that you do not release them here in this `update` method.  This is not good practice.  Yes, I see that you probably release them in your `process()` method, but it looks like there are paths through your code that would result in the `left` or `right` not being released.  Every time this happens, you lose that memory block forever.  If you run out of memory blocks, your audio will stop.  The way to check is to put a print statement in your main `loop()` function to watch your available memory.   You can watch your memory via:

```
Serial.print("MEM Cur/Pk: ");
Serial.print(AudioMemoryUsage_F32());
Serial.print("/");
Serial.print(AudioMemoryUsageMax_F32());
Serial.println();
```

* Finally, your approach of using `#ifdef FFT_Noise_Subtraction` is a good approach.  Unfortunately, you do not know if it is failing because of a memory leak (see previous bullet) or because the FFT / IFFT are failing, or because the NoiseReduction is failing.  I suggest that you continue this `#if` approach and put a `#if` just around the calls to the NoiseReduction itself.  In your code, add the `#if` and the `#endif` it look like the code below.  If you try that code, it will use the FFT and IFFT, but it will not use the NoiseReduction.  If the code fails, you know it is something *other* than the noise reduction.  If it works, then you know that your problem is the noise reduction.

```
 //convert to frequency domain
  myFFT_Right.execute(in_audio_block_right, complex_2N_buffer[0]);
  myFFT_Left.execute(in_audio_block_left, complex_2N_buffer[1]);

  AudioStream_F32::release(in_audio_block_right);
  AudioStream_F32::release(in_audio_block_left);
  //define some variables

#if 0
  noiseReduction_right.processAudioFD(complex_2N_buffer[0], myFFT_Right.getNFFT());  //in your derived class, overwrite this!!
  noiseReduction_left.processAudioFD(complex_2N_buffer[1], myFFT_Left.getNFFT());  //in your derived class, overwrite this!!
#endif

  //rebuild the negative frequency space
  myFFT_Right.rebuildNegativeFrequencySpace(complex_2N_buffer[0]); //set the negative frequency space based on the positive
  myFFT_Left.rebuildNegativeFrequencySpace(complex_2N_buffer[1]); //set the negative frequency space based on the positive
  
  //call the IFFT
  
  audio_block_f32_t *out_audio_block_right = myIFFT_Right.execute(complex_2N_buffer[0]); //out_block is pre-allocated in here.
  audio_block_f32_t *out_audio_block_left = myIFFT_Left.execute(complex_2N_buffer[1]); //out_block is pre-allocated in here.
```

Chip

michaelliesenberg, 2022-03-29:
Hi Chip thank you for the help.

i have changed the FFT_overlap_factor to 2
````
const int audio_block_samples = 128
const int FFT_overlap_factor = 2 
````

and set 
````
AudioMemory_F32(60, audio_settings);
````

Now if i uncomment
````
  noiseReduction_right.processAudioFD(complex_2N_buffer[0], myFFT_Right.getNFFT());  
  noiseReduction_left.processAudioFD(complex_2N_buffer[1], myFFT_Left.getNFFT());  
````
The audio signal is there but a with artefacts and if but the lines back, there is no audio signal coming anymore.

Here is the Init in constructor:
`````
  int N_FFT = audio_block_samples * FFT_overlap_factor;
  noiseReduction_right.setup(audio_settings, N_FFT);
  noiseReduction_left.setup(audio_settings, N_FFT);
  myFFT_Right.setup(audio_settings, N_FFT); 
  myFFT_Left.setup(audio_settings, N_FFT); 
  myIFFT_Right.setup(audio_settings, N_FFT); 
  myIFFT_Left.setup(audio_settings, N_FFT); 

  (myFFT_Right.getFFTObject())->useHanningWindow();
  (myFFT_Left.getFFTObject())->useHanningWindow();
  (myIFFT_Right.getFFTObject())->useHanningWindow();
  (myIFFT_Left.getFFTObject())->useHanningWindow();
  //Frequency processing
  noiseReduction_right.setAttack_sec(1);//10
  noiseReduction_left.setAttack_sec(1);
  noiseReduction_right.setRelease_sec(1); //3
  noiseReduction_left.setRelease_sec(1); 
  noiseReduction_right.setMaxAttenuation_dB(0); 
  noiseReduction_left.setMaxAttenuation_dB(0); //16
  noiseReduction_right.setSNRforMaxAttenuation_dB(1.0);//1
  noiseReduction_left.setSNRforMaxAttenuation_dB(1.0);
  noiseReduction_right.setTransitionWidth_dB(6.0); 
  noiseReduction_left.setTransitionWidth_dB(6.0); 
  noiseReduction_right.setGainSmoothing_sec(0.005);
  noiseReduction_left.setGainSmoothing_sec(0.005);
  noiseReduction_right.setEnableNoiseEstimationUpdates(true); 
  noiseReduction_left.setEnableNoiseEstimationUpdates(true); 

  myBlock_Right = allocate_f32_memory_help(0);
  if (myBlock_Right != NULL) AudioStream_F32::initialize_f32_memory(myBlock_Right, 0);
    myBlock_Left = allocate_f32_memory_help(1);
  if (myBlock_Left != NULL) AudioStream_F32::initialize_f32_memory(myBlock_Left, 1);
`````

And here is the code inside update for noise removal:
`````

 audio_block_f32_t *in_audio_block_right = myBlock_Right;
  audio_block_f32_t *in_audio_block_left = myBlock_Left;

  //convert to frequency domain
  myFFT_Right.execute(in_audio_block_right, complex_2N_buffer[0]);
  myFFT_Left.execute(in_audio_block_left, complex_2N_buffer[1]);

  AudioStream_F32::release(in_audio_block_right);
  AudioStream_F32::release(in_audio_block_left);
  
  //define some variables
  noiseReduction_right.processAudioFD(complex_2N_buffer[0], myFFT_Right.getNFFT());  //in your derived class, overwrite this!!
  noiseReduction_left.processAudioFD(complex_2N_buffer[1], myFFT_Left.getNFFT());  //in your derived class, overwrite this!!

  //rebuild the negative frequency space
  myFFT_Right.rebuildNegativeFrequencySpace(complex_2N_buffer[0]); //set the negative frequency space based on the positive
  myFFT_Left.rebuildNegativeFrequencySpace(complex_2N_buffer[1]); //set the negative frequency space based on the positive
  
  //call the IFFT
  
  audio_block_f32_t *out_audio_block_right = myIFFT_Right.execute(complex_2N_buffer[0]); //out_block is pre-allocated in here.
  audio_block_f32_t *out_audio_block_left = myIFFT_Left.execute(complex_2N_buffer[1]); //out_block is pre-allocated in here.

    for (int i=0; i<AUDIO_BLOCK_SAMPLES; i++) 
    {
      audiodata[0][i] = out_audio_block_right->data[i];  
      audiodata[1][i] = out_audio_block_left->data[i];   
    }
`````

Do you think i have to change the noise settings ? Does it record the noise at beginning or it subtracts the noise with the parameters on the struct?
And is it normal that once i do FFT and back iFFT i get some artefacts?

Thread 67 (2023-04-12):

Tympan/Tympan_Library #67: Using the AIC CODEC Shield as Main sound processor

zvikapika, 2023-04-12:
Hi,
Due to Tympan Rev E being sold out, I have been trying to connect the AIC CODEC Shield directly to a Teensy 4.1 board, with no luck. 
The connections I have made are according to the documentation and the Rev E PCB, as following:

Shield                                 |                       Connected To
**First row (from left)**
1.8V                                                                Voltage regulated 1.8V (stepped down from on 5V of Teensy)
IN1 RIGHT                                                      NC
IN1 Left                                                          NC
LINE OUT LEFT                                               NC
LINE OUT RIGHT                                            NC
GND                                                               Teensy GND

**Second row**
MIC BIAS                                                       NC
MCLK                                                            Teensy D23
BCLK                                                             Teensy D21
WCLK                                                            Teensy D20
GND                                                              Teensy GND

**Third row**
PDM CLK                                                       NC
PDM DAT                                                       NC
SDO                                                               NC
SDI                                                                 NC
SCK                                                                NC
CS                                                                  NC

**Fourth row**
3.3V                                                              Teensy 3.3V
DOUT                                                            Teensy D6
DIN                                                                Teensy D32
SDA2                                                             Teensy D18 (Wire2 changed to Wire, also tried Wire1)
SCL2                                                              Teensy D19 (same)
GND                                                              Teensy GND

Also, visual legend of the connections made can be found here:
https://www.dropbox.com/s/wg9cwudwld1ig52/AIC%20CODEC%20Shield%20Connections.png?dl=0

Upon loading the **AudioPassThru** sketch, I am getting no sound on the headphones connected to the shield, and serial monitor shows the following error messages:

AudioPassThru: Starting setup()...
AudioControlAIC3206: Received Error During goToPage(): Error = 2
AudioControlAIC3206: Received Error During goToPage(): Error = 2
AudioControlAIC3206: Received Error During writeRegister(): Error = 2
AudioControlAIC3206: Received Error During writeRegister(): Error = 2
AudioControlAIC3206: Received Error During writeRegister(): Error = 2
AudioControlAIC3206: Received Error During writeRegister(): Error = 2
AudioControlAIC3206: Received Error During writeRegister(): Error = 2
AudioControlAIC3206: Received Error During writeRegister(): Error = 2
AudioControlAIC3206: Received Error During writeRegister(): Error = 2
AudioControlAIC3206: Received Error During writeRegister(): Error = 2
AudioControlAIC3206: Received Error During writeRegister(): Error = 2
AudioControlAIC3206: Received Error During writeRegister(): Error = 2
AudioControlAIC3206: Received Error During writeRegister(): Error = 2
AudioControlAIC3206: Received Error During writeRegister(): Error = 2
AudioControlAIC3206: Received Error During writeRegister(): Error = 2
AudioControlAIC3206: Received Error During goToPage(): Error = 2
AudioControlAIC3206: Received Error During writeRegister(): Error = 2
AudioControlAIC3206: Received Error During writeRegister(): Error = 2
AudioControlAIC3206: Received Error During writeRegister(): Error = 2
AudioControlAIC3206: Received Error During writeRegister(): Error = 2
AudioControlAIC3206: Received Error During writeRegister(): Error = 2
AudioControlAIC3206: Received Error During writeRegister(): Error = 2
AudioControlAIC3206: Received Error During writeRegister(): Error = 2
AudioControlAIC3206: Received Error During writeRegister(): Error = 2
AudioControlAIC3206: Received Error During goToPage(): Error = 2
AudioControlAIC3206: Received Error During goToPage(): Error = 2
AudioControlAIC3206: Received Error During goToPage(): Error = 2
AudioControlAIC3206: Received Error During goToPage(): Error = 2
AudioControlAIC3206: Received Error During goToPage(): Error = 2
AudioControlAIC3206: Received Error During goToPage(): Error = 2
AudioControlAIC3206: Received Error During writeRegister(): Error = 2
AudioControlAIC3206: Received Error During writeRegister(): Error = 2
AudioControlAIC3206: Received Error During writeRegister(): Error = 2
AudioControlAIC3206: Received Error During writeRegister(): Error = 2
AudioControlAIC3206: Received Error During writeRegister(): Error = 2
AudioControlAIC3206: Received Error During writeRegister(): Error = 2
AudioControlAIC3206: Received Error During goToPage(): Error = 2
AudioControlAIC3206: Received Error During goToPage(): Error = 2
AudioControlAIC3206: Received Error During goToPage(): Error = 2
AudioControlAIC3206: Received Error During goToPage(): Error = 2
AudioControlAIC3206: Received Error During writeRegister(): Error = 2
AudioControlAIC3206: Received Error During writeRegister(): Error = 2
AudioControlAIC3206: Received Error During writeRegister(): Error = 2
AudioControlAIC3206: Received Error During writeRegister(): Error = 2
AudioControlAIC3206: Received Error During goToPage(): Error = 2
AudioControlAIC3206: Received Error During goToPage(): Error = 2
AudioControlAIC3206: Received Error During writeRegister(): Error = 2
AudioControlAIC3206: Received Error During writeRegister(): Error = 2
AudioControlAIC3206: Received Error During writeRegister(): Error = 2
AudioControlAIC3206: Received Error During writeRegister(): Error = 2
AudioControlAIC3206: Received Error During writeRegister(): Error = 2
AudioControlAIC3206: Received Error During writeRegister(): Error = 2
AudioControlAIC3206: Received Error During goToPage(): Error = 2
AudioControlAIC3206: Received Error During writeRegister(): Error = 2
AudioControlAIC3206: Received Error During writeRegister(): Error = 2
AudioControlAIC3206: Received Error During goToPage(): Error = 2
AudioControlAIC3206: Received Error During goToPage(): Error = 2
AudioControlAIC3206: Received Error During writeRegister(): Error = 2
AudioControlAIC3206: Received Error During writeRegister(): Error = 2
AudioControlAIC3206: Received Error During goToPage(): Error = 2
AudioControlAIC3206: Received Error During goToPage(): Error = 2
AudioControlAIC3206: Received Error During goToPage(): Error = 2
AudioControlAIC3206: Received Error During goToPage(): Error = 2
AudioControlAIC3206: Received Error During goToPage(): Error = 2
AudioControlAIC3206: INFO: Read Page.  Page: 0 Reg: 27.  Failed to go to read page.  Could not go there.
AudioControlAIC3206: Received Error During goToPage(): Error = 2
AudioControlAIC3206: Received Error During writeRegister(): Error = 2
AudioControlAIC3206: Received Error During writeRegister(): Error = 2
AudioControlAIC3206: Received Error During writeRegister(): Error = 2
AudioControlAIC3206: Received Error During writeRegister(): Error = 2
AudioControlAIC3206: Received Error During goToPage(): Error = 2
AudioControlAIC3206: Received Error During goToPage(): Error = 2
AudioControlAIC3206: Received Error During goToPage(): Error = 2
AudioControlAIC3206: Received Error During goToPage(): Error = 2
AudioControlAIC3206: Received Error During goToPage(): Error = 2
Setup complete.
Running...

If there is any way we can get this to work, I'd appreciate any help at all. This project is done during a hackathon in Nigeria taking place this week, and the team is very excited to see the project work. However, so far we haven't been able to do so...
Thanks in advance for any pointer or help,
Zvika

chipaudette, 2023-04-12:
Hello Zvika!

The type of errors that you're seeing tell me that the AIC3206 is not responding to the Teensy.  Typically, the problem is that the "reset" pin of the AIC3206 is not connected back to the processor (to the Teensy).  So, I looked at the connection map that you provided.  I think that I see the problem.  Or, at least, I see one problem.

```
**Second row**
MIC BIAS                                NC  -> No, connect to D36 (or to Gnd)
MCLK                                    Teensy D23
BCLK                                    Teensy D21
WCLK                                    Teensy D20
n_RESET_1                               You forgot this one!  This is critical!  Connect to D26!
GND                                     Teensy GND
```

I have not fully checked your other connections, but try making the changes above and let me know!

Chip

chipaudette, 2023-04-12:
Below is an explanation of the two changes above, for anyone that cares...

Regarding the MIC_BIAS connection:

- This change is not critical.  It is not the cause of your error messages.  But, once you get the system working, this change will help your system's audio inputs work correctly.
- The "MIC_BIAS" connection is an **input** to the AIC Shield, not an output from the shield.  It is intended to be connected back to a GPIO pin on your microcontroller.  The microcontroller sets it HIGH or LOW.  If it is left floating ("NC"), I don't know what will happen.
- The purpose of this line is to control whether mic bias is applied to the right input channel (IN_3_R).  The AIC itself must be commanded (via software command) to generate the mic bias voltage.  By default, though, the mic bias is only applied to the left channel (IN_2_R).  To have the AIC mic bias voltage also be applied to the right channel (IN_3_R), you must pull the "MIC_BIAS" pin high.  There is a command in the Tympan_Library to help with this.
- If you never want mic bias, and you do not want to connect it back to the microcontroller, you can simply tie this pin to GND

Regarding the n_RESET_1 pin:

- This change is critical.  The AIC will never work without making this change.
- The "n_RESET_1" pin is an input to the AIC Shield.  It must be connected back to the microcontroller.  It is used as part of the initialization and configuration process for the AIC (which is handled by the Tympan_Library)
- The details of how this pin is used is too complicated to describe here.  But, basically, the pin needs to be toggled by through various HIGH and LOW states during the initialization process.  Without a connection to the microcontroller, these HIGH and LOW transitions never happen, which means that the AIC never initializes.  As a result, the microcontroller cannot communicate with the AIC.  The failure to receive any replies from the AIC is what causes the errors that you are seeing.
- In short: you must connect this pin back to the Teensy

Chip

chipaudette, 2023-04-14:
If you're not getting any errors, but you're also not getting any audio, lots could be wrong.  I'd need to see a wiring diagram to help at this point:

* To which AIC pin are you injecting your audio?
*  Where is your audio coming from (a mic or your phone)?  
* Is your audio signal going into the AIC strong enough?  Maybe you should add some gain?
* To which pin are you listening for the audio coming out?
* How are you trying to listen to it (ear phones,  loud speaker,  Line-in on your PC)?

Chip

zvikapika, 2023-04-14:
hi Chip,
thanks again for the quick reply,

attaching the wiring scheme at the end of text, with a picture of the setup

we have tried using both amplified and non amplified stereo lapel microphone pair, connected to the shield via pink PL jack, 
and standard over-the-ear music headphones connected to the shield via black PL jack

if the audio input isn't strong enough, how would I know about it? 
I tried looking for sketches that test the microphone and the speaker separately, but could not find such.

By adding gain, you mean by software or hardware? I tried uploading the basicGain sketch, manually setting gain up to 0.95 (getting message on the serial monitor: servicePotentiometer: Digital Gain dB = 40.0) but still no audible sound was heard on the headphones

As for selecting the input source - you are right, I completely missed that. however I've tried the other two options, same result.

could it be that my earphones are the cause of the problem? Is there a way to test them separately?

Thanks again,
Zvika

Shield                                       Teensy 4.1

**First row (from left)**
1.8V                                         Voltage regulated 1.8V (stepped down from on 5V of Teensy)
IN1 RIGHT                                    NC
IN1 Left                                     NC
LINE OUT LEFT                                NC
LINE OUT RIGHT                               NC
GND                                          GND

**Second row**
MIC BIAS                                     D36
MCLK                                         D23
BCLK                                         D21
WCLK                                         D20
RESET                                        D26
GND                                          GND

**Third row**
PDM CLK                                      NC
PDM DAT                                      NC
SDO                                          NC
SDI                                          NC
SCK                                          NC
CS                                           NC

**Fourth row**
3.3V                                         3.3V
DOUT                                         D6
DIN                                          D32
SDA2                                         D18
SCL2                                         D19
GND                                          GND

[image]

biomurph, 2023-04-17:
@zvikapika 
This is exciting!
I will make a branch of the Tympan Rev E hardware git to modify the board to make this connection.

@chipaudette 
In 'normal' conditions, the AIC Shield is the secondary CODEC, but since this configuration doesn't have the main board CODEC, can the Teensy be connected with the primary pins? That would make this setup with the AIC Shield behave more like the Tympan E with no AIC Shield. Does that make sense?

zvikapika, 2023-04-17:
I am now running the 'OutputTone' sketch, which, if I understood correctly, is supposed to test the headphones / sound generation only, but no sound is heard (I checked the headphones with another audio source and they are OK)

Maybe continuing your question, 
Is the connection of the AIC shield directly to the Teensy according to the above scheme supposed to work just like the Tympan Rev E (without bluetooth)?
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

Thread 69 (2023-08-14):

Tympan/Tympan_Library #69: Equalizer

zvikapika, 2023-08-14:
Hi all,
We have now entered level 2 of the project, taking the prototype to an audiologist and then to some tests
I was asked to develop an equalizer app that would be used for the self-tune process
(here, in Nigeria, audiologist who know how to do this are quite rare)
The basic idea is to help a hearing impaired client to map his/her own frequency response values, and per (currently) 8 frequency bands find what is the threshold DB per band, so that we can compensate for the bands that need amplification
I searched the examples but could not find a similar example - I figured there must be one, since this is what a hearing aid does, right? So, either I missed it somehow, or it is code that was not included in the examples.
Can you help?
Thanks,
Zvika

biomurph, 2023-08-16:
@zvikapika 
This is totally doable with Tympan, but I don't think that we have any diagnostic code examples.
Full disclosure, I am primarily the hardware engineer on the Tympan project. 
The primary focus for Tympan has been as a development and testing platform for audio compression and other audio manipulation. There may be code for self-fitting hearing aid that could get you most of the way to your result?
Please check the examples that use the bluetooth app. They may be the best suited to build out your project idea.

@chipaudette @eyuan-creare 
Do you have any insight into Zvika's project idea?

zvikapika, 2023-08-16:
Thanks!

I just found this morning a correspondence regarding this need, in which Chip referred to the Equalizer_8BandBiquad example he wrote. I uploaded it but there is a lot of high pitch static noise when I do not speak directly to the microphone, making it impossible to work with. 

I tried attenuating the high pitch frequency channels through the Serial Monitor, as the sketch allows, but noise levels did not  change. 

I also thought it might be an issue with my microphone (using a lapel) but even after changing mic, noise level did not subside. 

@chipaudette 
Thoughts? ideas? 
Thanks!
Zvika

eyuan-creare, 2023-08-16:
Do you receive this high pitch noise when using the straight passthru example?  You could consider recording the sound to SD card before and after the 8-band filter.

zvikapika, 2023-08-17:
No, the pass thru example works fine. but after tweaking half a day with just about everything, I found that the issue was too much gain on the microphone. Simple! when you know it :) Thanks for all the help!
btw the equalizer example has a minor typo:

AudioConnection_F32       patchCord35(gainBlocks[4],0,mixer,4);   //connect gain block back to mixer
AudioConnection_F32       **patchCord36**(gainBlocks[5],0,mixer,5);   //connect gain block back to mixer
AudioConnection_F32       **patchCord36**(gainBlocks[6],0,mixer,6);   //connect gain block back to mixer
AudioConnection_F32       patchCord37(gainBlocks[7],0,mixer,7);   //connect gain block back to mixer

chipaudette, 2023-08-17:
Hi!

Thanks for pointing out the typo in the patchCord names.  I've fixed it in the repo.

Chip

zvikapika, 2023-08-17:
Oh, WOW! 
Dude, I cannot thank you enough for your insightful comments and references

Indeed I am working on a (low cost) hearing aid (for Nigerian market) - hence why we chose to work with a DIY Revision E rather then the earpiece (also, we opted not to use Bluetooth to make things simple for the end consumer). 

I know quite a bit about general microcontroller programming, mechatronics and such, but I am doing my first steps with audio processing. Still, I am currently technical project lead... Next week we will be meeting a local Audiologist with whom we will consult about the process of tuning such a device in more detail, but from an initial Zoom meeting I gathered that:

* The type of hearing impairment we wish to address is characterized by uneven frequency response of the patients, which is asymmetric i.e. not the same in both ears. 

* The process of tuning a device here is composed of playing certain frequencies at ascending volumes and marking at which volume level the patient started hearing the sound. Then, based on each volume registered per frequency, an equalizer is configured (per ear) so that it compensates for the patient's natural hearing impairment

* So, now after successfully modifying your Equalizer example to activate two separate equalizers for Left and Right channels, my goal is, pretty much like you guessed, to create a simple user interface that will allow for the patient to diagnose his/her natural frequency response and use that data as gain parameters for the stereophonic equalizer

Regarding lapels, I guessed that they we not ideal but I figured placing two microphones, one next to each ear, as you said, will give us a starting point. Also, I was looking a bit but count not find directional microphones that are compact - usually they are long and cumbersome, maybe due to reflector shape reasons. Anyway at first stage we thought of 3d printing a small cone reflector, but have not yet arrived at that point - see how that goes. Do you know where we can source a compact directional mic?

Last, regarding compression - it makes perfect sense, I know anything about it, though. I will read your post and try incorporating the example into the equalizer

Thank you so much again, I really appreciate your extensive help. 

Hopefully, this project will make a difference to many people's lives here in Nigeria whose need are currently not catered to at all, due to cost reasons

All the best,
Zvika

chipaudette, 2023-08-17:
Hi Zvika,

Here are some thoughts in response to your comments:

> The process of tuning a device here is composed of playing certain frequencies at ascending volumes and marking at which volume level the patient started hearing the sound. 

Yes, testing to find one's threshold of hearing is very typical.  But, despite being typical and normal, it is still hard to do if you are testing normal hearing people.  Very hard.

The problem is that normal hearing people are able to hear *very* quiet sounds.  Therefore, at the person's threshold of hearing, the test tones will be very quiet.  This has several important implications:

* The test must be conducted in a very, very quiet environment.  Any ambient noise could mask the quiet test tones.  The ambient noise must be quieter than your quiet test tones. 
 This is very hard.  Usually hearing testing is conducted in a sound-proof booth.  If you don't have a such a sound-proof booth, you will not get good measurements of hearing threshold for normal-hearing individuals.  

* The system generating the very quiet test tones must have very low self-noise.  Like with the need to block out ambient noise, the system generating the test tones must not project any audible electronic noise into the test area.  If the system produces any audible hiss, it might mask the very quiet test tones, which will degrade the test.

* If you are wearing a hearing device (such as the Tympan) and you are testing to confirm that you have improved a person's hearing thresholds, the hearing device must also produce very little electronic noise.  Otherwise, the device's own hiss might mask the very quiet test tones.  This will degrade the test.  The hearing device might be very useful in everyday life, where ambient noise levels are higher, but testing down at one's hearing threshold is a very challenging test environment.  You might find that the self-noise of the Tympan (or, more likely, the noise floor of the lapel microphones) might be too high to use a test method that is based on measuring the hearing thresholds.

> Do you know where we can source a compact directional mic?

I think that it is probably best to use omnidirectional microphones.  A directional microphone might be good if you can keep it pointing in the right direction...but which direction is the "right direction"?  In my message, I raised the possibility that you might inadvertently get a directional microphone as your lapel microphone.  I raised this possibility because it is a bad thing.  I would suggest that you stay with omnidirectional microphones.

zvikapika, 2023-08-18:
Thanks, again, for your enlightening comments! 

As the manual tuning of the devices can be anywhere, we cannot rely on a sound proof booth. For the time being we have settled for noise blocking earphones such as the ones used in workshops, that the patient will wear during the calibration process on top of the in-ear headphones/buds. Hopefully that would get us close enough to bring some value.

The generation of the test tones will also be done by the Tympan hardware, so I think it should be relatively noise free, from what I've so far heard.

Thanks again,
Zvika

p.s. I just got the first generation of the 3d printed ear reflectors, you might want to take a look :)
https://www.dropbox.com/s/xhlpnnfk1efk47v/20230818_095406.jpg?dl=0
https://www.dropbox.com/s/drwdgtlofds0az1/20230818_095446.jpg?dl=0
they still need more work ...

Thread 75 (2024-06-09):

Tympan/Tympan_Library #75: Sample rates set below 9888hz cause incorrect MCLK generation that leads to sample rate problems

coreysmccall, 2024-06-09:
In `Tympan_Library/src/output_i22_F32.cpp`, the `AudioOutputI2S_F32::config_i2s()` function generates the MCLK signal by setting up PLL4 ("audio clock") and SAI1 dividers. This MCLK signal then determines the effective sampling rate of the codec.

Unfortunately, the minimum sample rate for the equations currently in this function is 9888Hz. If 9887Hz or lower is used, it causes the SAI1 post divider `n2` to be > 64, which is too large for the 6-bit register that holds it (CCM_CS1CDR_SAI1_CLK_PODF). This is an issue for 8KHz (or below) audio applications.  

You can observe the actual sample rate by probing WCLK (same frequency as sample rate) or checking the time between when audio blocks are ready. For example, if you set `sample_rate_Hz = 8000.0f`, the actual resulting sample rate is 40,000Hz because of the overflow. 

To resolve: can `n1 = 8` be used instead of `n1 = 4` for the SAI1 pre-divider? This will allow for sample rates down to 4944Hz. It will also limit the max sample rate from 1,265,625Hz to 632,812Hz. At least on my Tympan Rev:E, I cannot sample above this new limit without problems anyways though, even with a large block size like 256.
 
I am not sure if changing this has any other implications. The `PaulStoffregen/Audio` library uses SAI1 pre divider = 4, but that library is not designed to easily change sample rates like this one is.

coreysmccall, 2024-06-09:
I can submit a pull request if you don't think that changing the SAI1 pre-divider like above will have another consequence. It seems to work for me.

chipaudette, 2024-06-11:
Thanks for finding this issue!

Let me take a look today and I'll let you know...

Chip

chipaudette, 2024-06-12:
I have confirmed that this is an issue.  Using the example 02-Utility/OutputTone.ino:
  * Using sample rates of 10 kHz and higher, it correctly produces 1 kHz tones
  * Using a sample rate of 8 kHz, it produces wildly wrong tones

coreysmccall, 2024-06-12:
Thanks for looking into this @chipaudette. Let me know if you would like me to open a PR (If allowed, I have not contributed here before). On mine, I just changed this SAI1 pre-divider to 8 instead of 4 in config_i2s() so that < 9888 hz works.

chipaudette, 2024-06-12:
I'm actively working it right.  Using 8 seems to work, which is great...but it fails again if one tries a sample rate of 4943 or lower, as you said.

I'm trying to modify the library so that it dynamically adjusts n1 in order to keep n2 at a value of 64 or below.  Unfortunately, the system doesn't seem to work if I keep increasing n1 above 8 (ie, a value of 10 and 12 don't seem to work).  So, that's a bummer.

I'm still working it...

chipaudette, 2024-06-12:
In testing the code by ear via my consumer-level earbuds, lowering the sample rate does allow background noise to appear.  I'm hearing hiss as the sample rate is dropped below 8 kHz.

To my ear, the frequency content of the noise starts in the high frequencies and then adds more lower-frequency content as the sample rate is lowered.  

IMO, what I'm hearing is probably best characterized as being "out of band" noise (ie, noise above Nyquist) that becomes audible only because the above-Nyquist frequencies finally get low enough to be easily heard once the sample rate drops below 8 kHz.

chipaudette, 2024-06-12:
Well, I can't figure out why it's not working with n1 = 10 or 12.  It seems stuck with a max of n1 = 8.

I've committed my changes to the repo.  It'll now auto-select n1 depending upon what sample rate you request.  As a result, it now works down to a sample rate of 4988 or so.  I'd like to to work at even lower sample rates, but at least it's better than it was.

Thanks for finding this issue!

coreysmccall, 2024-06-12:
Sounds good. Yes, a more general fix would be better. 

So, n1 SAI1 (pre-divider is only 4 bits unfortunately, [IMXRT1060 manual page 1056](https://www.pjrc.com/teensy/IMXRT1060RM_rev3.pdf)).

The other constrain I see is the minimum output of the MCLK generator since PLL4 needs to output between 650 and 1300MHz ([IMXRT1060 manual page 1028](https://www.pjrc.com/teensy/IMXRT1060RM_rev3.pdf))). So, of MCLK must be 64x the actual sample rate, the minimum MCLK is

650MHz -> ANALOG_PLL_AUDIO_POST_DIV (/4) -> SAI1 PRE DIVIDED (/8) -> SA1 POST DIVIDER (/64) -> ACTUAL SAMPLE RATE (/64) = 4,959Hz.

I haven't listened to the 8KHz audio enough yet to know if it should sound better than an idea 8KHz audio source. We will test some more here.

chipaudette, 2024-06-12:
Oh, man, that's a good find!  650 MHz minimum!  Dang!

coreysmccall, 2024-06-12:
Yes, it is 3 bits sorry for the typo. Maybe there's an alternative way to get below 4,959Hz actual sample rate, but for now this should be low enough for most audio applications. 8KHz was just excluded before.

chipaudette, 2024-06-12:
Can we close this issue?

coreysmccall, 2024-06-13:
Thanks, I'm closing it since it works on 8khz now. Thank you for the quick fix!!

I see the commit- It fixes the original problem (letting the post divider overflow), but now the input divider (n1) is susceptible to the same issue if the sample rate is set lower than 4,959Hz. We gained a lower sample rate minimum now though which fixes this particular issue. I think it's the best we can do without heavy lifting because of the PLL constraints. Thanks again!

closed 2024-06-13 by coreysmccall

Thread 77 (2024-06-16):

Tympan/Tympan_Library #77: Sitrep - try every example for compile errors, run errors (Rev F)

stvhawes, 2024-06-16:
New to the project, so while familiarising myself with the code I tried every (non-deprecated) example.  

The compile-fails especially could be my libraries setup rather than any particular issue.  Run errors perhaps because there was a hardware item I should have plugged in...

# Compiles and runs and query-favourite
   ./03-Intermediate/WDRC_FIR_8Band/WDRC_FIR_8Band.ino                       okay  serial monitor in + out
   ./05-FullSystems/WDRC_8BandFIR_full/WDRC_8BandFIR_full.ino      okay  serial monitor in and out
             also tested sweep .. good
   ./06-AppTutorial/BasicGain_wApp/BasicGain_wApp.ino                      okay  serial monitor out

# Compiles and runs, no problemo
   ./01-Basic/BasicGain/BasicGain.ino                            okay  serial monitor out
   ./01-Basic/TrebleBoost/TrebleBoost.ino                        okay  serial monitor out
              CPU Cur/Pk: 0.6%/0.6%, MEM Cur/Pk: 4/6, FreeRAM(B) 499712
   ./01-Basic/TrebleBoost_wComp/TrebleBoost_wComp.ino            okay  serial monitor out
               printGainStatus: Input PGA = 20.0 dB. Compressor Gain (L/R) = 0.0, 0.0 dB.
               CPU Cur/Pk: 2.2%/2.3%, MEM Cur/Pk: 4/8, FreeRAM(B) 499712
   ./01-Basic/AudioPassThru/AudioPassThru.ino                    okay  serial monitor out
   ./01-Basic/PrintCPUandMemoryUsage/PrintCPUandMemoryUsage.ino  okay  serial monitor out
               CPU Cur/Pk: 0.4%/0.4%, MEM Cur/Pk: 4/6, FreeRAM(B) 499712
   ./01-Basic/ChangeSampleRate/ChangeSampleRate.ino              okay  serial monitor out
   ./02-Utility/SD_Card/SDWriter_wApp_wMTP/SDWriter_wApp_wMTP.ino    okay  serial monitor in + out
   ./02-Utility/SD_Card/SDWavPlayer/SDWavPlayer.ino
        * For access to WAV files, please visit https://www.pjrc.com/teensy/td_libs_AudioDataFiles.html.
       repeat loop: Starting audio player: SDTEST1.WAV  
   ./02-Utility/SD_Card/SDWriter/SDWriter.ino
            To Start Recording: Turn the volume pot all the way up.
            To Stop Recording: Turn the volume pot all the way down.
            serviceMicDetect: detected removal of plug-in microphone. On-board PCB mics now active.   
   ./02-Utility/MyAudioAlgorithm/MyAudioAlgorithm.ino                       okay  serial monitor out
   ./02-Utility/RamWavPlayer/RamWavPlayer.ino                              okay  serial monitor out
         Starting sample 'YES'...len = 12000 samples
         Starting sample 'NO'...len = 12000 samples   
   ./02-Utility/ControlViaSerial/ControlViaSerial.ino                      okay  serial monitor in and out
   ./02-Utility/OutputTone/OutputTone.ino                                  okay  serial monitor out
      Changing to start tone, amplitude = 0.01
      Changing to start silence...
      Changing to start tone, amplitude = 0.03
   ./02-Utility/LongAudioBlocks/LongAudioBlocks.ino                        okay  serial monitor out
          : Sample rate = 44100.00 Hz
          : block size = 1024 samples per channel
         CPU Cur/Pk: 0.5%/0.5%, MEM Cur/Pk: 4/6
   ./02-Utility/Bluetooth/Tympan_Test_BLE_nRF52/Tympan_Test_BLE_nRF52.ino  okay  serial monitor in and out
   ./02-Utility/Bluetooth/Tympan_Test_BLE/Tympan_Test_BLE.ino              okay  serial monitor in and out
         serialManager: BLE: Name from module = Tympan-6D4E   
   ./04-FrequencyDomain/NoiseReduction_FD/NoiseReduction_FD.ino             okay  serial monitor in and out
   ./03-Intermediate/Equalizer_8BandBiquad/Equalizer_8BandBiquad.ino         okay  serial monitor in + out
   ./04-FrequencyDomain/FrequencyCompression_FD/FrequencyCompression_FD.ino   okay  serial monitor in and out
   ./04-FrequencyDomain/GenericFreqDomainExample_FD/GenericFreqDomainExample_FD.ino   okay  serial monitor in and out   
   ./06-AppTutorial/TrebleBoost_wComp_wApp/TrebleBoost_wComp_wApp.ino      okay  serial monitor out
   ./06-AppTutorial/TrebleBoost_wApp/TrebleBoost_wApp.ino                  okay  serial monitor out
   ./06-AppTutorial/TrebleBoost_wApp_Alt/TrebleBoost_wApp_Alt.ino          okay  serial monitor out
         still: TrebleBoost_wApp: Starting setup()   needs 'alt'
         *   example, which was "TrebleBoost_wApp".   
         *   As a tutorial on how to interact with the mobile phone App, you should first explore the previous
   ./06-AppTutorial/BasicGain_wApp/BasicGain_wApp.ino                      okay  serial monitor out

   ./08-Earpieces/EarpieceManualMixing_wSD/EarpieceManualMixing_wSD.ino      okay  serial monitor out
   ./08-Earpieces/OutputTone_wEarpieces/OutputTone_wEarpieces.ino                 okay  serial monitor out
   ./08-Earpieces/AudioPassThru_wEarpieces/AudioPassThru_wEarpieces.ino          okay  serial monitor out
add aic shield...  earbuds in shield's output
   ./07-AIC_Shield/TrebleBoost_wComp_Quad/TrebleBoost_wComp_Quad.ino         okay  serial monitor out
   ./07-AIC_Shield/SDWriter_Quad_wApp/SDWriter_Quad_wApp.ino         okay  serial monitor out + in
   ./07-AIC_Shield/AudioPassThru_Quad/AudioPassThru_Quad.ino                 okay  serial monitor out

# Compiles, errors during run
   ./02-Utility/SD_Card/SDWriter_wApp_wLog/SDWriter_wApp_wLog.ino
            Setup: SD configured for 2 channels.
            error: setup: SD begin failed!
            SdError: 0X17,0X0   
[... 103 lines cut ...]
         BTNRH_PresetManager_UI.h:43: warning: unused variable 'old_n_crossover' 
            43 |       int old_n_crossover = old_n_chan-1;
               |           ^~~~~~~~~~~~~~~
         In file included from /Stephen/tympan-repo/libraries/Tympan_Library/examples/05-FullSystems/WDRC_NBand_Stereo_Earpiece_Prescrip_wApp/WDRC_NBand_Stereo_Earpiece_Prescrip_wApp.ino:67:
         /Stephen/tympan-repo/libraries/Tympan_Library/examples/05-FullSystems/WDRC_NBand_Stereo_Earpiece_Prescrip_wApp/BTNRH_PresetManager_UI.h: In member function 'virtual bool BTNRH_StereoPresetManager_UI::processCharacterTriple(char, char, char)':
         BTNRH_PresetManager_UI.h:554: warning: comparison of constant '0' with boolean expression is always false 
           554 |         delay(10); if (flag_fail < 0) { setIncrementChannelsMessage("Failed"); } else { setIncrementChannelsMessage("Complete");}
      Running eg...
         BTNRH_WDRC: Preset_SD_Base: beginSD_wRetry: *** WARNING ***: cannot open SD. sd.begin(SD_CONFIG) = 0
             : Trying again...
         BTNRH_WDRC: Preset_SD_Base: beginSD_wRetry: *** WARNING ***: cannot open SD. sd.begin(SD_CONFIG) = 0
             : FAILED all attempts.  Returning w..

# Deprecated
   ./08-Earpieces/Deprecated/WDRC_XBand_PrescripSave_wApp/WDRC_XBand_PrescripSave_wApp.ino   Deprecated
   ./02-Utility/Bluetooth/Deprecated (RevD, RevE)/ChangeBaudrate/ChangeBaudrate.ino    Deprecated
   ./02-Utility/Bluetooth/Deprecated (RevD, RevE)/BC127LibraryTest/BC127LibraryTest.ino    Deprecated
   ./02-Utility/Bluetooth/Deprecated (RevD, RevE)/BasicGain_wApp_BLEdebug/BasicGain_wApp_BLEdebug.ino    Deprecated
   ./02-Utility/Bluetooth/Deprecated (RevD, RevE)/BluetoothAudio_PassThru/BluetoothAudio_PassThru.ino    Deprecated
   ./02-Utility/Bluetooth/Deprecated (RevD, RevE)/EchoBLE/EchoBLE.ino    Deprecated
   ./02-Utility/Bluetooth/Deprecated (RevD, RevE)/BC127Terminal/BC127Terminal.ino    Deprecated
   ./02-Utility/Bluetooth/Deprecated (RevD, RevE)/BLELibraryTest/BLELibraryTest.ino    Deprecated
   ./05-FullSystems/Deprecated/WDRC_8BandFreqWarpFIR/WDRC_8BandFreqWarpFIR.ino    Deprecated
   ./05-FullSystems/Deprecated/WDRC_3BandIIR_wAFC/WDRC_3BandIIR_wAFC.ino    Deprecated
   ./05-FullSystems/Deprecated/WDRC_8BandIIR_wAFC/WDRC_8BandIIR_wAFC.ino    Deprecated

stvhawes, 2024-06-16:
I don't think there's any urgency since there are awesome working examples.

I'll try my hand at some fixes.  Some are probably already fixed (tests were on 12 June main-branch), and if not then very likely to be addressed before I get to them.

chipaudette, 2024-06-16:
Hi!  Thanks for this work!

Most of your errors are caused by running an example setup for using an SD card in your Tympan, but you must not have an SD card.  If you used an SD card, more than half your errors would go away.

Also, you got an error on the example for renaming the Bluetooth module. As the comments in the code say, and as your own comment say, this example only works for older versions of the Tympan.  It is not indebted for use with Rev F.

You also got a bunch of errors on the Deprecated examples. These are not expected to work. Instead of calling them "deprecated", I probably should have called them "soon to be deleted".

Finally, there are all of the other errors that you found. These are more troubling and surprising to me. Prior to the release of Rev F, I recompiled all of these myself and they all worked at that time.  I'll go back and try to recompile them myself in the next couple days.  

What tool chain were you using to compile and test all of these?  You didn't do them all manually like I did, did you?  You must have done the testing in some automated manner? Did you set up a continuous integration system?  I'm very curious!

Chip

stvhawes, 2024-06-21:
:) manual.  Felt like a good way to sense the scale and breadth of the library, while looking for a few favourite examples to focus on.

Also, I didn't expect you would have been able to watch all the examples on every update.  Automation would be nice but not easy when there's the specific hardware (and past versions of the hardware).  Benefit to audiologists would the key purpose of the library rather than software complexity..

I have yet to fix anything .. but I did make a fork and try out the PR pathway.

stvhawes, 2024-06-23:
Yep, sourcing a microSD did fix the runtime issues, and really brought my Tympan on!

Meanwhile I've run through the compile-issues and worked out a proposed fix for each.  I've tested as best I can but might have misunderstood the purpose and capabilities of an example (so incomplete fix).

Pull request: https://github.com/Tympan/Tympan_Library/pull/78

chipaudette, 2024-06-26:
Nice Pull Request!  Thanks so much for the fixes!

stvhawes, 2024-06-27:
Ty.  Closed.

closed 2024-06-27 by stvhawes

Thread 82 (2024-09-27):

Tympan/Tympan_Library #82: First Time Programming - Teensy Loader stalls at 2%

eyuan-creare, 2024-09-27:
Loading Basic Gain w/App on new Tympan (that @biomurph previously loaded with Basic Gain)
- Stalls at 2%; No blinking light.  Not responding to serial.  No audio output.
[image]

- When I press the Auto button, Teensy Loader downloads firmware successfully.  I verified basic gain is working with app control.
 ```
12:06:42.384 (loader): Auto Button event
12:06:42.385 (loader): Auto mode: enabled
12:06:42.403 (loader): File "C:\Users\eyuan\AppData\Local\Temp\arduino\sketches\5565D6EC6055986BFBB5CC9B3AC67DF1\BasicGain_wApp.ino.hex", 185344 bytes
12:06:42.409 (loader): File "BasicGain_wApp.ino.hex". 185344 bytes, 2% used
12:06:42.418 (loader): begin elf_guess_size
12:06:42.419 (loader): found elf file
12:06:42.421 (loader): read elf files into memory, 4529776 bytes
12:06:42.422 (loader): elf appears to be for Teensy 4.1 (IMXRT1062) (8126464 bytes)
12:06:42.422 (loader): elf binary data matches hex file
12:06:42.425 (loader): elf file is for Teensy 4.1 (IMXRT1062) (id=25)
12:06:42.427 (loader): using hex file
12:06:42.436 (loader): begin operation
```

chipaudette, 2024-09-27:
Did this event happen using the questionable unit?

chipaudette, 2024-09-27:
Were you compiling with MTP enabled (Tools->USB Type->"Serial w MTP (experimental)")?  Or, were you using the basic plain-vanilla USB Serial (Tools->USB Type->"Serial")?

eyuan-creare, 2024-09-27:
The sketchy Tympan TYM-F003, is now working.  

When first plugged in today, no USB ports showed up on the Tympan .  After compiling Basic Gain, it failed to upload.  Then I pressed the program button and it uploaded successfully.  After that, I compiled Basic Gain w/App and it uploaded fine.

chipaudette, 2024-09-27:
We just talked by phone.  You'll keep an eye on them as you work with them over today and Monday. I'll be in on Monday/Tuesday to update their BLE firmware and we can also explore this programming issue.

eyuan-creare, 2024-09-27:
@biomurph If you get the chance, could you try compiling and uploading the example Gain w/App onto a few fresh Tympans?

As I was able to eventually program them (by working thru the Teensy Loader directly) I don't think this is critical.  But good to keep an eye on and also to archive in case users hit this problem.

eyuan-creare, 2024-09-27:
Chip, what version is the ne BT firmware?  I'll log this to Snipe for the (4) units you already updated

eyuan-creare, 2024-09-27:
Something to try if the Tympan does not show up in the Arduino IDE with a serial port.  Taken from Teensy website.  Run the [serial driver installer](https://www.pjrc.com/teensy/serial_install.exe).

```
On Windows, even if the [serial driver installer](https://www.pjrc.com/teensy/serial_install.exe) has run correctly, sometimes Windows will retain old information in its registry and fail to load the driver. The Device Manager will show "USB Serial" with an error, instead of "USB Serial (Communication Class, Abstract Control Model)" with a COM port number assigned.

These actions usually can cause Windows to re-detect the device and begin using the correct driver.

- Run the serial installer program again, or run the Teensyduino installer and use the update driver option on the first step.
- Click that "Update Driver" button in the device manager. If the driver installer has run, Windows should be able to find the driver.
- Plug the cable into a different USB port. The Windows Registry handles each physical port with separate registry entries.
- Do and/all of the above with or without the device connected. Sometimes Windows will do things differently if the device is present or absent.
- ```

biomurph, 2024-09-27:
@eyuan-creare 
When I am preparing and testing Tympans I use Teensy Loader to flash precompiled HEX of BasicGain.ino
After the Loader is done, I see the Tympan appear on the serial port, and I also verify both mics with headphones.

I have found that Teensy units can sometimes require having the program button pressed or occasionally require power down/up.

eyuan-creare, 2024-09-27:
The first time programming 4 fresh units took several cycles of powering on/off, pressing program button.  Perhaps try compiling a sketch and program one unit in the typical fashion, then press the program button.  That sequence did not work on several units.

biomurph, 2024-09-30:
@eyuan-creare 
I popped open a Tympan from my inventory.
It powered up and connected to the serial port just fine.
I compiled and uploaded the BasicGain sketch, which opened Teensy Loader and successfully erased and programmed the Tympan.

One thing to check is to make sure that your USB cable is plugged all the way into the Tympan.
When you plug in, make sure that the charge LED is lit?
I just noticed that I had to push hard to get the USB micro to seat all the way in.

eyuan-creare, 2024-09-30:
@biomurph Thanks for giving this a try. I'll close this issue until I see it pop up again.

closed 2024-09-30 by eyuan-creare

biomurph, 2024-09-30:
@eyuan-creare 
I just powered down the Tympan I successfully programmed, and then powered up and pressed the program button.
Upload by teensy loader was successful. I can’t replicate your problem yet.

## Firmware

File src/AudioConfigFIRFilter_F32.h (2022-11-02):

/*
   AudioConfigFIRFilter_F32

   Created: Chip Audette, OpenAudio, Sept 2021
     Primarly built upon CHAPRO "Generic Hearing Aid" from
     Boys Town National Research Hospital (BTNRH): https://github.com/BTNRH/chapro

   License: MIT License.  Use at your own risk.

*/

#ifndef _AudioConfigFIRFilter_F32_h
#define _AudioConfigFIRFilter_F32_h

#include <Arduino.h>


class AudioConfigFIRFilter_F32 {
    //GUI: inputs:0, outputs:0  //this line used for automatic generation of GUI node
    //GUI: shortName:config_FIR
  public:
    AudioConfigFIRFilter_F32(void) {}
    AudioConfigFIRFilter_F32(const AudioSettings_F32 &settings) {}

    int designLowpass(int n_fir, float freq_Hz, float sample_rate_Hz, float *filter_coeff);
    int designBandpass(int n_fir, float freq1_Hz, float freq2_Hz,  float sample_rate_Hz, float *filter_coeff);
    int designBandstop(int n_fir, float freq1_Hz, float freq2_Hz, float sample_rate_Hz, float *filter_coeff);
    int designHighpass(int n_fir, float freq_Hz, float sample_rate_Hz, float *filter_coeff);
    int designPassOrStop(int is_bandpass, int n_fir, float freq1_Hz, float freq2_Hz, float sample_rate_Hz, float *filter_coeff);

    void createWindow(int window_type, int n_window, float *window_coeff) {
      createWindow(window_type, n_window, n_window, window_coeff);
    }
    void createWindow(int window_type, int n_window_orig, int n_window, float *window_coeff);
    
  protected:

    //used for nextPowerOfTwo
    const int n_out_vals = 10;
    int out_vals[10] = {8, 16, 32, 64, 128, 256, 512, 1024, 2048, 4096};
    int nextPowerOfTwo(int n) {
      if (n < out_vals[0]) return out_vals[0];
      for (int i = 1; i < n_out_vals; i++) {
        if ((n > out_vals[i - 1]) & (n <= out_vals[i])) {
          return out_vals[i];
        }
      }
      return n;
    }
};

#ifndef fmove
#define fmove(x,y,n)    memmove(x,y,(n)*sizeof(float))
#endif
#ifndef fcopy
#define fcopy(x,y,n)    memcpy(x,y,(n)*sizeof(float))
#endif
#ifndef fzero
#define fzero(x,n)      memset(x,0,(n)*sizeof(float))
#endif

#include "utility/BTNRH_rfft.h"

inline int AudioConfigFIRFilter_F32::designLowpass(int n_fir, float freq_Hz, float sample_rate_Hz, float *filter_coeff) {
  float freq1_Hz = 0.0;     //low edge of bandpass
  float freq2_Hz = freq_Hz; //high edge of bandpass
  return designBandpass(n_fir, freq1_Hz, freq2_Hz, sample_rate_Hz, filter_coeff);
}
inline int AudioConfigFIRFilter_F32::designHighpass(int n_fir, float freq_Hz, float sample_rate_Hz, float *filter_coeff) {
  float freq1_Hz = freq_Hz;            //low edge of bandpass
  float freq2_Hz = sample_rate_Hz/2.0; //high edge of bandpass
  return designBandpass(n_fir, freq1_Hz, freq2_Hz, sample_rate_Hz, filter_coeff);
}
inline int AudioConfigFIRFilter_F32::designBandpass(int n_fir, float freq1_Hz, float freq2_Hz, float sample_rate_Hz, float *filter_coeff) {
  int is_bandpass = 1; //one for bandpass
  return designPassOrStop(is_bandpass, n_fir, freq1_Hz, freq2_Hz, sample_rate_Hz, filter_coeff);
}
inline int AudioConfigFIRFilter_F32::designBandstop(int n_fir, float freq1_Hz, float freq2_Hz, float sample_rate_Hz, float *filter_coeff) {
  int is_bandpass = 0; //zero for bandstop
  return designPassOrStop(is_bandpass, n_fir, freq1_Hz, freq2_Hz, sample_rate_Hz, filter_coeff);
}

//wt = window type.  0 = Hamming, 1 = blackman, else = Hanning
//nw_orig = length of the window
//nw = number of coefficients (could be larger than nw_orig
//ww = array of window coefficients
inline void AudioConfigFIRFilter_F32::createWindow(int wt, int nw_orig, int nw, float *ww) {
  //float sm = 0.0;
  float w, p;
  float a = 0.16f;  //for blackman window
  
  for (int j = 0; j < nw; j++) ww[j] = 0.0f; //clear
  for (int j = 0; j < nw_orig; j++) {  //create window
    p = M_PI * (2.0 * j - nw_orig) / nw_orig;
    if (wt == 0) {
      w = 0.54 + 0.46 * cos(p);                   // Hamming
    } else if (wt == 1) {
      w = (1.0 - a + cos(p) + a * cos(2.0 * p)) / 2.0;  // Blackman
    } else {
      //win = (1 - cos(2*pi*[1:N]/(N+1)))/2;  //WEA's matlab call, indexing starts from 1, not zero
      w = (1.0 - cosf(2.0 * M_PI * ((float)(j)) / ((float)(nw_orig - 1)))) / 2.0;
    }
    //sm += w;
    ww[j] = (float) w;
  }  
}

inline int AudioConfigFIRFilter_F32::designPassOrStop(int is_bandpass, int n_fir, float freq1_Hz, float freq2_Hz, float sample_rate_Hz, float *filter_coeff) {

  //remap the names to match BTNRH example
  int nw_orig = n_fir;       //use BTNRH name
  float sr = sample_rate_Hz; //use BTNRH name
  const int wt = 0;          //window type (BTNRH name): 0 = Hamming, 1=Blackmann, 2 = Hanning

  //make sure that the requested n_fir fits within what we know how to do
  if ((nw_orig < 1) || (nw_orig > out_vals[n_out_vals - 1])) return -1;

  int      nt, nf, ns;
  int      bp_inds[2];
  int      nw = nextPowerOfTwo(nw_orig);
  
  //Serial.print("AudioConfigFIRFilter_F32: designLowpass: nw_orig = "); Serial.print(nw_orig);
  //Serial.print(", nw = "); Serial.println(nw);

  //we're going to design this FIR filter using an FFT

  nt = nw * 2;   //we're going to do an fft that's twice as long (zero padded)
  nf = nt/2 + 1; //number of bins to nyquist in the zero-padded FFT.
  ns = nf * 2;   //hold complex data

  float ww[nw];
  float xx[ns];
  float yy[ns];
  
  //initilize (clear) the arrays
  fzero(xx, ns); fzero(yy, ns);
  
  // create windowing function
  createWindow(wt, nw_orig, nw, ww);

  // define the frequency bounds (in FFT indices) that we care about
  bp_inds[0] = max(0,min(nf, round(nf * freq1_Hz * (2.0 / sr))));
  bp_inds[1] = max(0,min(nf, round(nf * freq2_Hz * (2.0 / sr))));

  // begin building the desired frequency response
  xx[nw_orig / 2] = 1.0; //make a single-sample impulse centered on our eventual window
  BTNRH_FFT::cha_fft_rc(xx, nt); //convert to frequency domain

  //check for special cases of the bandstop
  if (is_bandpass == 0) { //look for if it is a bandstop
    if ((bp_inds[0]==0) && (bp_inds[1] < nf)) {
      //if the bandstop starts at 0, this is actually a highpass
      bp_inds[0] = bp_inds[1]; 
      bp_inds[1] = nf;
      is_bandpass = 1; //it's not a bandstop anymore, it's a bandpass (as a highpass)
    } else if ((bp_inds[0]>0) && (bp_inds[1] == nf)) {
      //if bandpass ends at nyquist, this is actually a lowpass
      bp_inds[1] = bp_inds[0];
      bp_inds[0] = 0;
      is_bandpass = 1;//it's not a bandstop anymore, it's a bandpass (as a lowpass)
    }
  }
  

  // create the desired response from the spectrum by copying just the desired regions of the impulse
  // int nbins = (be[k + 1] - be[k]) * 2;  Serial.print("fir_filterbank: chan ");Serial.print(k); Serial.print(", nbins = ");Serial.println(nbins);
  if (is_bandpass==1) {
    //copy the values between the two limits
    fcopy(yy + bp_inds[0] * 2, xx + bp_inds[0] * 2, (bp_inds[1] - bp_inds[0]) * 2); //copy just our passband
  } else {
    //copy the low coefficients
    fcopy(yy + bp_inds[1] * 2, xx + bp_inds[1] * 2, (nf - bp_inds[1]) * 2); //copy the low end below the bandstop
    
    //copy the high coefficients
    fcopy(yy + bp_inds[1] * 2, xx + bp_inds[1] * 2, (nf - bp_inds[1]) * 2); //copy the high end above the bandstop
  }
  
  // convert back to time domain
  BTNRH_FFT::cha_fft_cr(yy, nt); //IFFT back into the time domain

  // apply window to iFFT of bandpass
  for (int j = 0; j < nw; j++) yy[j] *= ww[j];
  
  //copy the filter coefficients to the output array
  fcopy(filter_coeff, yy, nw_orig);

  return 0;  //OK
}

#endif

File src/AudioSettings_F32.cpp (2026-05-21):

#include "AudioSettings_F32.h"
#include "AudioStream_F32.h"

float AudioSettings_F32::get_cpu_load_divide_fac(void) { // return devide_fac for: CPU_percent = n_cycles / divide_fac
	float foo2 = 0.0f;
	#if defined(KINETISK)
		//teensy 3.6...modified from Teensy3/AudioStream.h
		//n is the number of cycles
		//#define CYCLE_COUNTER_APPROX_PERCENT(n) (((n) + (F_CPU / 32 / AUDIO_SAMPLE_RATE * AUDIO_BLOCK_SAMPLES / 100)) / (F_CPU / 16 / AUDIO_SAMPLE_RATE * AUDIO_BLOCK_SAMPLES / 100))
		foo2 = (float)( F_CPU/16 ) / sample_rate_Hz;
		foo2 *= ((float)audio_block_samples);
		foo2 /= 100.f;
	#else
		//teensy 4...modified from Teensy4/AudioStream.h
		//n is the number of cycles
		//#define CYCLE_COUNTER_APPROX_PERCENT(n) (((n) + (F_CPU_ACTUAL / 128 / AUDIO_SAMPLE_RATE * AUDIO_BLOCK_SAMPLES / 100)) / (F_CPU_ACTUAL / 64 / AUDIO_SAMPLE_RATE * AUDIO_BLOCK_SAMPLES / 100))
		foo2 = (float)( F_CPU_ACTUAL/64 ) / sample_rate_Hz;
		foo2 *= ((float)audio_block_samples);
		foo2 /= 100.f;
	#endif
	return foo2;
}

float AudioSettings_F32::cpu_load_percent(const int n) { //n is the number of cycles
/*
	#if defined(KINETISK)
	//teensy 3.6...modified from Teensy3/AudioStream.h
	//#define CYCLE_COUNTER_APPROX_PERCENT(n) (((n) + (F_CPU / 32 / AUDIO_SAMPLE_RATE * AUDIO_BLOCK_SAMPLES / 100)) / (F_CPU / 16 / AUDIO_SAMPLE_RATE * AUDIO_BLOCK_SAMPLES / 100))
	//
	// Re-expressed, the equation above looks like:  CPU_percent = n / divide_fac + 0.5
	// The "+ 0.5" at the end is so that (in the historical code) it would *round* to the nearest integer (not truncate).
	// We're returning a float, so we don't care about this rounding.  We'll leave it out.
	// https://forum.pjrc.com/index.php?threads/cpu-cycle-counter-formula-in-audiostream.63898/
	
	float foo1 = 0;
	//foo1 += ((float)(F_CPU / 32))/sample_rate_Hz;
	//foo1 *= ((float)audio_block_samples);
	//foo1 /= 100.f;
	foo1 += (float)n;
	float foo2 = (float)(F_CPU / 16)/sample_rate_Hz;
	foo2 *= ((float)audio_block_samples);
	foo2 /= 100.f;
	return  foo1 / foo2;

	//return (((n) + (F_CPU / 32 / sample_rate_Hz * audio_block_samples / 100)) / (F_CPU / 16 / sample_rate_Hz * audio_block_samples / 100));

	#else
	//teensy 4...modified from Teensy4/AudioStream.h
	//n is the number of cycles
	//#define CYCLE_COUNTER_APPROX_PERCENT(n) (((n) + (F_CPU_ACTUAL / 128 / AUDIO_SAMPLE_RATE * AUDIO_BLOCK_SAMPLES / 100)) / (F_CPU_ACTUAL / 64 / AUDIO_SAMPLE_RATE * AUDIO_BLOCK_SAMPLES / 100))
	//
	// Re-expressed, the equation above looks like:  CPU_percent = n / divide_fac + 0.5
	// The "+ 0.5" at the end is so that (in the historical code) it would *round* to the nearest integer (not truncate).
	// We're returning a float, so we don't care about this rounding.  We'll leave it out.
	// https://forum.pjrc.com/index.php?threads/cpu-cycle-counter-formula-in-audiostream.63898/
	
	float foo1 = 0;
	//foo1 +=((float)(F_CPU_ACTUAL / 128))/sample_rate_Hz;
	//foo1 *= ((float)audio_block_samples);
	//foo1 /= 100.f;
	foo1 += (float)n;
	float foo2 = (float)(F_CPU_ACTUAL / 64)/sample_rate_Hz;
	foo2 *= ((float)audio_block_samples);
	foo2 /= 100.f;
	return  foo1 / foo2;	
	#endif
*/

	return (float(n) / get_cpu_load_divide_fac());
}

float AudioSettings_F32::processorUsage(void) { 
	return cpu_load_percent(AudioStream::cpu_cycles_total); 
};
float AudioSettings_F32::processorUsageMax(void) { 
	return cpu_load_percent(AudioStream::cpu_cycles_total_max); 
}
void AudioSettings_F32::processorUsageMaxReset(void) { 
	AudioStream::cpu_cycles_total_max = AudioStream::cpu_cycles_total; 
}

unsigned long AudioSettings_F32::millis(void) {
	// return milliseconds as counted by the number of calls to AudioStream_F32::update_all() 
	// instead of the regular millis() that is based on the CPU clock.  This is perhaps better
	// if the processor is being put to sleep (such as via "asm volatile("wfi");"), which
	// means that the typical Arduino "millis()" will not be accurate anymore.
	uint32_t n_audio_blocks = AudioStream_F32::update_counter;
	double millis_per_block = ((double)audio_block_samples / (double)sample_rate_Hz) * 1000.0;
	return (unsigned long)((n_audio_blocks * millis_per_block)+0.5);
}

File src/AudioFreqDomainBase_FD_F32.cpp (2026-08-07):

#include "AudioFreqDomainBase_FD_F32.h"
//#include <arm_math.h>

int AudioFreqDomainBase_FD_F32::setup(const AudioSettings_F32 &in_settings, const int _N_FFT, const int _N_IFFT) {
	sample_rate_input_Hz = in_settings.sample_rate_Hz;  //sample rate for in-coming data
	bool flag_reallocate_complex_buffer = false;

	//setup the FFT and IFFT.  If they return a negative FFT, it wasn't an allowed FFT size.
	int prev_N_FFT = N_FFT;
	if (prev_N_FFT != _N_FFT) {
		N_FFT = myFFT.setup(in_settings, _N_FFT); //hopefully, we got the same N_FFT that we asked for
		if (N_FFT < 1) {
			if (flag_printDebug) print_ptr->println(F("AudioFreqDomainBase_FD_F32: FAILED setting up myFFT for N_FFT = ") + String(_N_FFT) + "...");
			return -1;
		}
		flag_reallocate_complex_buffer = true;
	}
	

	int prev_N_IFFT = N_IFFT;
	if (prev_N_IFFT != _N_IFFT) {
		float32_t ratio_IFFT_to_FFT = static_cast<float32_t>(_N_IFFT)/static_cast<float32_t>(_N_FFT);
		AudioSettings_F32 out_settings = in_settings;
		out_settings.sample_rate_Hz = in_settings.sample_rate_Hz * ratio_IFFT_to_FFT;
		out_settings.audio_block_samples = static_cast<int>(in_settings.audio_block_samples * ratio_IFFT_to_FFT + 0.5f); // the +0.5f is to make the cast become a rounding
		N_IFFT = myIFFT.setup(out_settings, _N_IFFT); //hopefully, we got the same N_IFFT that we asked for
		if (N_IFFT < 1) {
			if (flag_printDebug) print_ptr->println(F("AudioFreqDomainBase_FD_F32: FAILED setting up myIFFT for N_IFFT = ") + String(_N_IFFT) + "...");
			return -1;
		}
		sample_rate_output_Hz = out_settings.sample_rate_Hz;
		audio_block_output_samples = out_settings.audio_block_samples;
		flag_reallocate_complex_buffer = true;
	}
	
	//decide windowing
	(myFFT.getFFTObject())->useHanningWindow(); //applied prior to FFT
	#if 1
		if (myIFFT.getNBuffBlocks() > 3) (myIFFT.getIFFTObject())->useHanningWindow(); //window again after IFFT
	#endif

 	if (flag_printDebug) {
		//print info about setup
		print_ptr->println(F("AudioEffectFreqShift_FD_F32: FFT parameters..."));
		print_ptr->print("    : N_FFT Requested = "); print_ptr->print(_N_FFT); print_ptr->print(", Actual = "); print_ptr->println(N_FFT);
		print_ptr->print("    : N_IFFT Requested = "); print_ptr->print(_N_IFFT); print_ptr->print(", Actual = "); print_ptr->println(N_IFFT);
		print_ptr->print("    : audio_block_samples = "); print_ptr->println(in_settings.audio_block_samples);
		print_ptr->print("    : FFT N_BUFF_BLOCKS = "); print_ptr->println(myFFT.getNBuffBlocks());
		print_ptr->print("    : IFFT N_BUFF_BLOCKS = "); print_ptr->println(myIFFT.getNBuffBlocks());
		print_ptr->print("    : FFT use window = "); print_ptr->println(myFFT.getFFTObject()->get_flagUseWindow());
		print_ptr->print("    : IFFT use window = "); print_ptr->println((myIFFT.getIFFTObject())->get_flagUseWindow());
		delay(30);  //give time for the print_ptr to spool out on slower systems
	}
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

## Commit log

2017-04-24 AudioControlTest: add print of coherent sum
2017-05-01 Hardware: adding files for enclosure
    [10000167 rev3.step, 10000167 rev3.stl, 10000200_r2.step, 10000200_r2.stl]
2017-05-22 Adding 3D CAD for PCB
    [7146-0012_PCB_Rev-A.STP, Lion Ion Battery.stl, Lithium Ion Battery.step]
2017-05-31 Update ChangeSampleRate.ino
    Changing input from on board microphone to microphone jack
2017-05-31 Update PrintCPUandMemoryUsage.ino
    Changing input from on board mic to mic jack
2017-05-31 Update TrebleBoost.ino
    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
2017-05-31 Update TrebleBoost_wComp.ino
    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
2017-08-30 Moved Unrelated Files To Separate Repos
    [10000167 rev3.step, 10000167 rev3.stl, 10000200_r2.step, 10000200_r2.stl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]
2017-10-30 manual teensy boards.txt
2018-02-12 Minor informational edits
    added color of audio ports
    added warning to take off headphones when changing modes
    suggestion: should we add a diagram of the Tympan + Teensy system to just above the Hardware section?
2018-03-14 RecordQueue: increasing queue depth
    Increasing queue depth from 53 (the value from the original Teensy Audio library?) to a depth of 100. As we're often using this queue object to buffer while writing to an SD card, the deeper queue de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
2018-05-23 Tympan.h: add println (commented) for debugging
2018-05-23 AIC3206: enable headphone charge pump!
2018-05-23 include teensy AudioControl.h in src/
    This AudioControl.h was copied from the teensy Audio library. It is the only file Tympan needs from the teensy Audio library. Including it here in /src prevents Tympan from unnecessarily including th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
2018-05-24 AIC3206: comments. changing charge pump rate.
2018-05-31 Replace AudioControl.h with TeensyAudioControl.h
    Doing this to avoid any namespace issues.
2018-06-04 Examples: removing printing of Int16 AudioMemory from Basic examples
2018-06-05 AudioFilterBiquad: make sample rate dependent
2018-06-07 Tympan.h: add stereoMic pin, add USB and BT Serial
2018-06-10 Examples: update AFC with HP filtering
2018-06-10 AIC3206: partial (failed) addition of HP filtering in AIC
2018-06-10 AIC3206: enabled on-board highpass filtering
2018-06-10 Examples: update AFC examples using ADC HP filtering
2018-06-25 TympanBase: enable it to print to BT and USB serial
2018-06-26 Example: SoundLevelMeter: adjust the cal for PCB mics
2018-07-09 Tympan: improve Serial reseting and printing
2019-01-14 AIC3206: fix a case with single AIC
2019-04-25 Examples: fix name givin in first print statement
2019-04-28 Change TLV320AIC3206 to AIC3206 to dodge conflict with Teensy Audio library
2019-04-30 pin defines updated but nee verification
2019-05-01 Quad: copy Teensy Audio files in
2019-05-01 AIC3206: improve compatibility with Teensy Audio
2019-05-02 first pass at pin changes for new hardware
2019-05-15 Fix Travis CI build. Explicitly point the Tympan library to the Teensy versions of the Audio and SD libraries.
2019-07-08 Changed examples to the right POT_PIN number
    Verified that the Tympan.h pin defines are correct for Tympan RevD
2019-07-27 SD: rename ISR to compile with Teensyduino 1.46
    Check impact on SD recording!
2019-08-15 Partial Attempt at Teensy 4 compatibility
2019-08-20 Fix synth_sine for Teensy4
2019-08-20 Turn off setting I2S freq for custom sample rate
2019-08-20 Make compatibility with Teensyduino 1.47
2019-08-21 Update Travis continuous integration builder to use an equivalent of the latest version of the Teensyduino loader.
2019-08-23 Travis CI: include local directories for all arduino sketches.
2019-08-23 Only test the pegged teensy platform version for now
2019-08-23 Setup AIC to work with digital PDM microphone
    control_aic3206.cpp
    -The PDM mic (IM69D130) has a max clock frequency of 3.3MHz. To half the PDM frequency (provided by the ADC_MOD_CLK), the clock divisor "NADC" was increased from 2 to 4. To keep the sample rate the s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
    TympanPDMMics.ino
    -Allowed the serial manager to switch to the digital PDM mics.
    Note, this has been tested on a Rev-C Tympan with PDM Mic (IM69D130) under sample frequencies of 8kHz to 48kHz)
2019-08-23 Added spreadheet of AIC clocks (related to PDM mic)
    [Spreadsheet of AIC Clocks.xlsx]
2019-09-16 AIC3206: enable Wire1 (for Teensy4)
2019-11-13 Refactor Tympan.h, add cpp, add printCPUandMem
2019-11-13 Examples\Basics: switch to new built-in printCPU method
2019-12-05 Examples: Intermediate WDRC_FIR_8Band switch to PCB mics
2020-05-12 IIR Filterbank: compiles!
2020-05-14 AudioSummer8: fix inability to access top 4 slots
2020-05-14 FreqWeighting_IEC1672: now uses correct sample rate
2020-05-15 AudioSDWriter: enable asking of current filename
2020-06-01 AICShield: correct resetAIC pin number to 42
2020-06-08 AudioFilterIIR_F32: add method to reset filter states.
2020-06-09 IIRFilterBank: improve debugging println
2020-06-09 IIR Filterbank: turn off some debug
2020-06-12 FeedbackCancel: add print for fdbk model
2020-06-12 IIR Filterbank: add debug println()s
2020-07-08 EchoBLE: test BC127 BLE functionality
    An initial test to verify BC127 BLE functionality and interoperability with iOS devices. Once BLE connections are established, ASCII input from an iOS device should be echo'd back by the Tympan.
    Begins: #26
2020-07-10 AudioPassThru_Quad: remove unneeded pin declarations
2020-08-17 Correct Typo in HP Filter
    Coefficient value shoud be shifted 8bits., as in the other coefficient settings.
2020-10-16 Set BC127 to use BLE mode for android devices.
2020-10-21 update pins to most latest hardware prototype
2020-10-24 Teensy4: fix imrxt ref for set_audioClock
2020-10-24 Tympan RevE: fix a couple pin names
2020-10-31 T4: variable sample rate works! (on T4)
2020-11-15 Output_I2S_quad: works! (fixed block size and sample rate)
2020-12-18 The sending of the header FAILS when this line is uncommented. Why? Time to check my arduino and teensyduino environment.
2020-12-23 myTympan.print => Serial.print. Instead of sending some basic logging to both the USB serial and the BLE with myTympan.print, let's just send it to the USB serial.
2021-02-18 Clearing some debug printlns
2021-03-30 AudioStream_F32: add Arduino.h to get String type
2021-04-01 BLE: remove some println
2021-04-01 Tympan: make FreeRam() work for Teensy4
2021-05-24 BLE: fix isConnected() and add printing of version
2021-05-26 BLE: clarify println in isAdvertising() message
2021-06-07 Tympan: assume BLE is default. Turn off regular printing to BT serial.
2021-06-07 FreqShift: beginning to fix the 75% overlap case?
2021-06-12 Examples: Move PDMMics from basic to utility
    [Spreadsheet of AIC Clocks.xlsx]
2021-06-14 Examples: FreqCompression: fix text in printHelp
2021-07-06 Update to accomodate Rev D board variant
    Rev D 0 and Rev D 1 use different pins for Shield function. These changes are specific to the CCP/Dosimeter production build
2021-07-06 fixed minor bug in pin settings
2021-07-15 Removed forceToDataMode call.
    This works as a hardware mechanism for switching to data mode, according to the Melody docs.
    It doesn't seem to like RevE:V7 devices... Maybwe we have the wrong GPIO pin in our RevE definition?
    PIO5 is listed as pin 2, but maybe it's 4?
    Either way, the software way to swith modes for V5 and V6 and V7 is to send '$$$$' with a delay before and after. The BLE library should probably rely on this method anyway.
2021-07-19 Update software version and hardware for RevE release
    Arduino 1.8.15
    Teensyduino 1.54
    Support RevE and RevD in the documentation
2021-08-01 FIR and IIR filter: split update() into update() and processAudioBlock()
2021-08-01 AudioFiltlerbank: add filter_order to state
2021-08-03 TympanRemoteFormatter: expand capacity via using linked lists instead of pre-allocated arrays
2021-08-03 AudioFilterFIR: move code to cpp, add printCoeff
2021-08-03 AudioFilterBank: clarify n_filters, dynamically create FilterbankDesigner
2021-08-05 AudioEffectCompWDRC: adding config methods, adding processAudioBlock(), improving handling of sample rate
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2021-08-11 AudioEffectCompBankWDRC_F32: fix printing of WDRC params to Serial Monitor
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2021-08-22 BC127: disable printing of error if there is no BLE Link ID
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2021-09-05 Examples: WDRC_8BandFIr_Stereo_wApp: correct the filter order to 96
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2021-09-23 output_i2s: fix table of sample rates
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2021-11-04 SpectrumAndCepstrum: Fix arrangement of functions in printResults.h
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2023-06-29 Corrected register page error for ADC filter that is different for the AIC3212. Tested and analyzed using SD recording.
2023-07-03 After last bugfix, forgot to return the AIC register settings to Book-0 in case subsequent commands assume that.
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2023-12-13 AudioPlayMemory: fix scaling of int16 to float. Add debugging println
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2024-02-15 Arduino 2.x: Tweaks to remove compiler errors and warnings
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2024-05-01 Case Consistency: continue to fix _f32 items
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2024-10-02 CalibrateAnalogIO: fix typo in comment
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2026-05-22 AudioStream_F32: replace Serial with user-changeable "print_ptr"
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
